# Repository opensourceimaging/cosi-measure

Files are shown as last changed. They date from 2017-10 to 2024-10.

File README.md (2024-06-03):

# COSI Measure

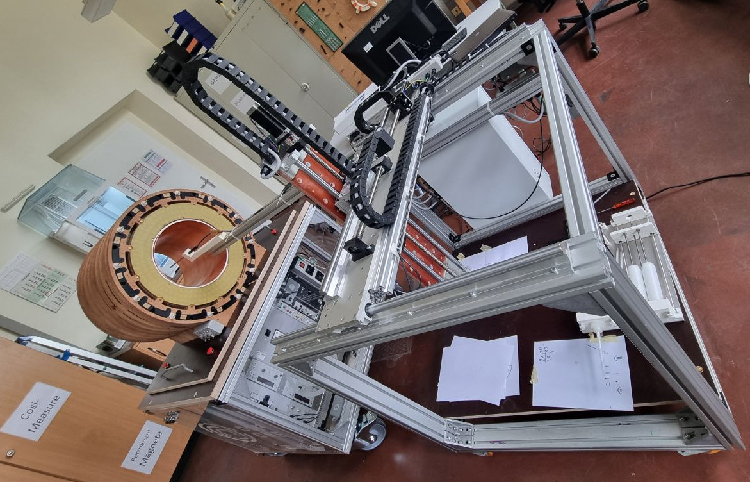
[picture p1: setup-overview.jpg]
COSI Measure


<!-- TOC -->

- [COSI Measure](#cosi-measure)
    - [Description](#description)
    - [System specifications](#system-specifications)
    - [Versions and Branches](#versions-and-branches)
    - [Contacts](#contacts)
        - [Known builds](#known-builds)
    - [Contributors alphabetical order](#contributors-alphabetical-order)
    - [Publications](#publications)
    - [Acknowledgments](#acknowledgments)
    - [License and Liability](#license-and-liability)

<!-- /TOC -->
## Description

COSI Measure is an open source multipurpose 3-axis robot operating in a large volume, that can be equipped with e.g. field mapping probes for static or dynamic field measurements (electromagnetic, temperature etc.). Submillimeter fidelity and reproducibility/backlash performance were evaluated experimentally. It can be potentially upgraded to be used as a CNC, for 3D printing or other applications, that require reproducible submillimeter movements.

## System specifications 

- Dimension: (80x90x105)cm³
- Working volume: (53x53x64)cm³
- Precision: positioning error <1mm
- Max load: ~20kg
- Applied force: 896N (91kg)
- Standalone system
- Inductive limit switches
- Emergency Stop
- Open Source Software GUI (Python)
- Estimated material costs: ~2000€

More photos and videos can be found on opensourceimaging.org: https://www.opensourceimaging.org/project/cosi-measure/ 

## Versions and Branches

You're currently viewing the `main` branch, showing ongoing development on `v2.0.*` of the COSI Measure system.\
New versions are developed in dedicated feature branches and then merged here.

The latest stable release is [v2.0](https://github.com/opensourceimaging/cosi-measure/releases/tag/v2.0).

For older, please check out the [releases overview](https://github.com/opensourceimaging/cosi-measure/releases/).

The changes between versions are summarzized in the respective release notes and documented in the [CHANGELOG](CHANGELOG.md) document.

## Contacts

General contact:
Name | Email | Institution | COSI Measure Applications
-----|-----|-----|-----|
Lukas Winter | lukas.winter@ptb.de | Physikalisch-Technische Bundesanstalt (PTB), Berlin, Germany | Magnetic field mapping of MR magnets, implant safety measurements, RF field mapping of RF coils using time-domain H- and E-field sensors, Measurements within an MR scanner, 3D printing

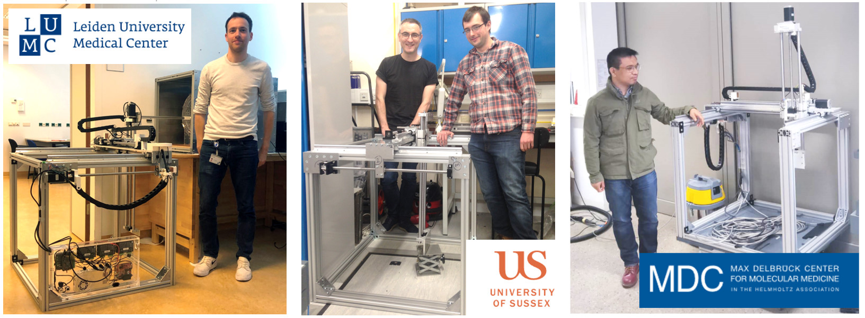
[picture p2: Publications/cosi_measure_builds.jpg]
COSI Measure Builds


### (Known) builds
Name | Email | Institution | COSI Measure Applications
-----|-----|-----|-----|
Haopeng Han | haopeng.han@mdc-berlin.de | Max-Delbrück Center for Molecular Medicine, Berlin, Germany | Temperature and RF field mapping of RF coils
Tom O'Reilly | t.o_reilly@lumc.nl | Leiden University Medical Center (LUMC), Leiden, Netherlands | Magnetic field mapping of low field MR magnets
Benjamin Menküc | benjamin.menkuec@fh-dortmund.de | University of Applied Sciences, Dortmund, Germany | Magnetic field mapping of low field MR magnets
Mark Bason | M.Bason@sussex.ac.uk | Quantum Systems and Devices, University of Sussex, Falmer, England | Magnetic field measurements
Wolfgang Kilian | Wolfgang.Kilian@ptb.de | Physikalisch-Technische Bundesanstalt (PTB), Berlin, Germany | 3D printing of phantoms

## Contributors (alphabetical order)
Nils Allek, Mark Bason, Jan Gregor Frintz, Haopeng Han, Amjad Kasabashy, Wolfgang Kilian, Ilia Kulikov, Benjamin Menküc, Tobias Mohr, Reiner Montag, Tom O'Reilly, David Shiers, Berk Silemek, Karl Stupic, Lukas Winter

## Publications
If you find this useful in your work, please cite:
[H. Han, R. Moritz, E. Oberacker, H. Waiczies, T. Niendorf and L. Winter, "Open Source 3D Multipurpose Measurement System with Submillimetre Fidelity and First Application in Magnetic Resonance", Scientific Reports, 7:13452, 2017](www.nature.com/articles/s41598-017-13824-z)

## Acknowledgments

This work is supported by the Open Source Imaging Initiative (OSI²), https://www.opensourceimaging.org/project/cosi-measure/

The project (21NRM05) has received funding from the European Partnership on Metrology, co-financed by the European Union's Horizon Europe Research and Innovation Programme and by the Participating States.

## License and Liability
The content in this repository is licensed under the CERN Open Hardware Licence Version 2 - Weakly Reciprocal, please see [LICENSE](LICENSE) for details and also check the [DISCLAIMER](DISCLAIMER.pdf)

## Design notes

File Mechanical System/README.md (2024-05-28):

# Mechanical System

Here you can find all necessary files to reproduce the COSI Measure mechanical setup.

Please read the assembly documentation first, in particular you will find some known issues or useful ideas in the comments section, which will help you reproducing the design.

## Folder: Aluplates
3D CAD models and technical drawings of the individual components.

## Folder: Complete System
3D CAD model of the complete system.

## Folder: Limit switch holder
3D CAD models of the limit switch holders

Please note that the following assembly instruction has not been updated yet to the new limit switch holders. For the new design refer to this pictures:

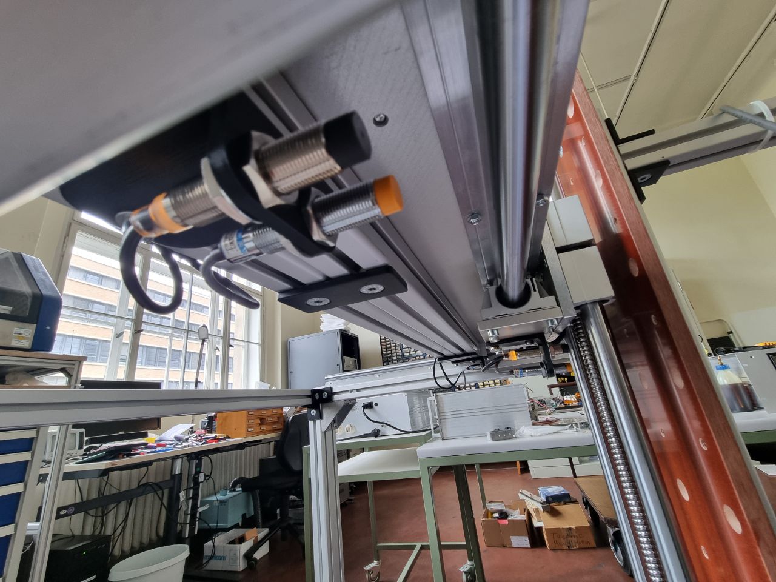
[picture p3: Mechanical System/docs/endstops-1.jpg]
Endstops 1


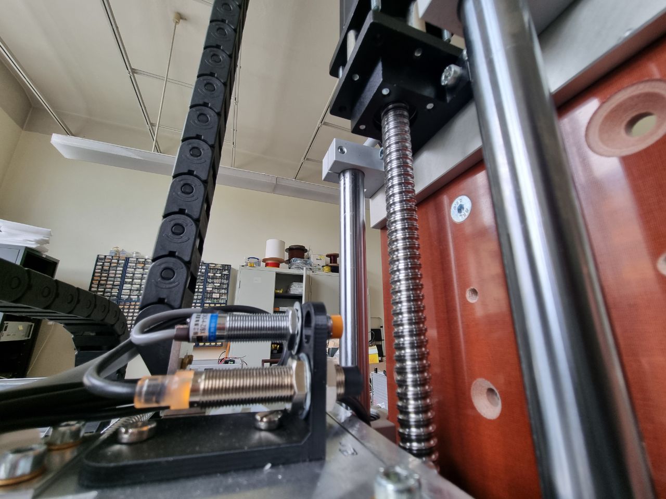
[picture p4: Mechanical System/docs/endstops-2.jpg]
Endstops 2


The outer limit switch is triggering the safe-torque-off (aka emergency stop). Thus the machine can not kill itself no matter what the software is trying to execute.

## Files: *_BoM_mechanical.ods and *_BoM_mechanical.pdf
Bill of material file for the mechanical setup. The .ods file can be opened with LibreOffice Calc (https://www.libreoffice.org/, the open source counterpart to Excel)

## Files: *_mechanical_assembly_instructions.odt and *_mechanical_assembly_instructions.pdf
Mechanical step by step assembly documentation. The .odt file can be opened with LibreOffice Writer (https://www.libreoffice.org/, the open source counterpart to Word).

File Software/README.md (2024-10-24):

# Software Getting Started

<!-- TOC -->

- [Software Getting Started](#software-getting-started)
    - [Installation](#installation)
        - [Download and Install Klipper](#download-and-install-klipper)
        - [Setting things up!](#setting-things-up)
        - [Config File](#config-file)
        - [Going into Bootloader Mode](#going-into-bootloader-mode)
        - [Flashing MCU and getting new Serial Port](#flashing-mcu-and-getting-new-serial-port)
    - [Commandline Interface](#commandline-interface)
    - [Python Software](#python-software)

<!-- /TOC -->

COSI Measure is using the open source 3D-printer firmware [klipper](https://www.klipper3d.org/). This document leads you through the installation. It´s assumed you have already installed [Raspberry-Pi-OS](https://www.raspberrypi.com/software/). We recommend the latest 64-bit Desktop version.

## Installation 

This Quick-Start-Guide is a short summary of https://www.klipper3d.org/Installation.html with some modifications for Rumba32 boards.

### 1. Download and Install Klipper

     git clone https://github.com/Klipper3d/klipper
     ./klipper/scripts/install-octopi.sh

Go to [devices/flash_mcu.sh](devices/flash_mcu.sh) and change the path in line 19 to the path of the repository above. For me line 19 is 

     19:  cd /home/cosi/klipper

### 2.1 Setting things up!

     cd klipper
     make menuconfig 

Opens a menu. Set
- Enable extra low-level configuration options
- Micro-controller Architecture (STMicroelectronics STM32)
- Processor model (STM32F446)
- Bootloader offset (32KiB bootloader)
- Clock Reference (12 MHz crystal)
- Communication interface (USB (on PA11/PA12))
- USB ids (doesnt matter. But choose something)
- no GPIO pins to set at startup ()

### 2.2 Config File

Get or write a ```printer.cfg```-file, here is mine: [devices/printer.cfg](devices/printer.cfg)

Save it as a file named "printer.cfg" in the home directory of the pi user (i.e. ```/home/cosi/printer.cfg```).

This file contains all machine configurations. Further reading: https://www.klipper3d.org/Installation.html#obtain-a-klipper-configuration-file

### 3. Going into Bootloader Mode

If not already done, install ```pigpio```for controlling the GPIO pins via the command line: 

     sudo apt-get install pigpio
     sudo systemctl enable pigpiod
     sudo systemctl start pigpiod

The shell script ```devices/flash_mcu.sh``` will set the Rumba board into bootloader mode and eventually will try to flash the MCU. Execute 

     ./backend/flash_mcu.sh

to set the board into bootloader mode. Because it doesn´t know yet the usb-id of the microcontroller it will fail to flash - ignore that for now. Search the Device ID by executing 

     lsusb

This will show up something like

     Bus 002 Device 001: ID 1d6b:0003 Linux Foundation 3.0 root hub
     Bus 001 Device 031: ID 0483:df11 STMicroelectronics STM Device in DFU Mode
     Bus 001 Device 002: ID 2109:3431 VIA Labs, Inc. Hub

So in my installatiom ```0483:df11``` is the ID of the STM-chip of Rumba32. Change line 20 in ```devices/flash_mcu.sh``` to your device ID and save the file.

### 4. Flashing MCU and getting new Serial Port

Execute ```devices/flash_mcu.sh``` again. Now it shall flash the MCU. This will eventually look something like

     Downloading to address = 0x08008000, size = 29236
     Download	[=========================] 100%        29236 bytes
     Download done.
     File downloaded successfully
     Transitioning to dfuMANIFEST state
     dfu-util: can't detach
     Resetting USB to switch back to runtime mode
     cosi@raspberrypi:~/klipper $ 

Then search for serial ports by executing 

     ls /dev/serial/by-id/*

this will return something similar to 

     /dev/serial/by-id/usb-Klipper_stm32f446xx_280058000951363131343032-if00

Copy and paste it in ```/home/cosi/printer.cfg``` to your MCU serial definition:

     [mcu]
     serial: /dev/serial/by-id/usb-Klipper_stm32f446xx_280058000951363131343032-if00

Congratulations, now you´re done. Get a coffee. Enjoy.

## Commandline Interface

Start the klipper service with executing

     sudo service klipper start

Klipper can be controlled via the following virtual serial port:

     /tmp/printer

Use 250000 Baud for communication. You can send G-code to this serial port and receive status information of the machine, refer to https://www.klipper3d.org/G-Codes.html. 

There are some custom g-code macros for disabling and enabling the drives without letting klipper loose it´s homing, for details see [printer.cfg](devices/printer.cfg) and [driver breakoutboard](../electronic-cabinet/Rumba32/Driver_BreakoutBoard/README.md). Use this commands only at standstill and never run a movement with disabled drives as this would eventually lead to false positioning.

Stop the klipper service by executing

     sudo service klipper stop

## Python Software

A python software to control CosiMeasure and a Lakeshore gaussmeter in an easy-to-use manner was developed. To get startet have a look into

     1_measurement_playground.ipynb

and 

     2_analyzing-demo.ipynb

Enjoy your day :-)

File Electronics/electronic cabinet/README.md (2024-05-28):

# COSI Measure Electronic Controls

In this folder are all the files you need to rebuild the electronic cabinet of COSI Measure. In every subfolder is a README.md as a landing page with detailed information on every subsystem.

# Building Instructions

1. Buy all needed stuff, see [bom-electronic-cabinet.csv](bom-electronic-cabinet.csv). <br>Keep in mind that there are some things missing that most of the labs have laying around e.g. screws, cables...

2. Machine all holes in the enclosure and the door, see drawings below <br>  <br> 

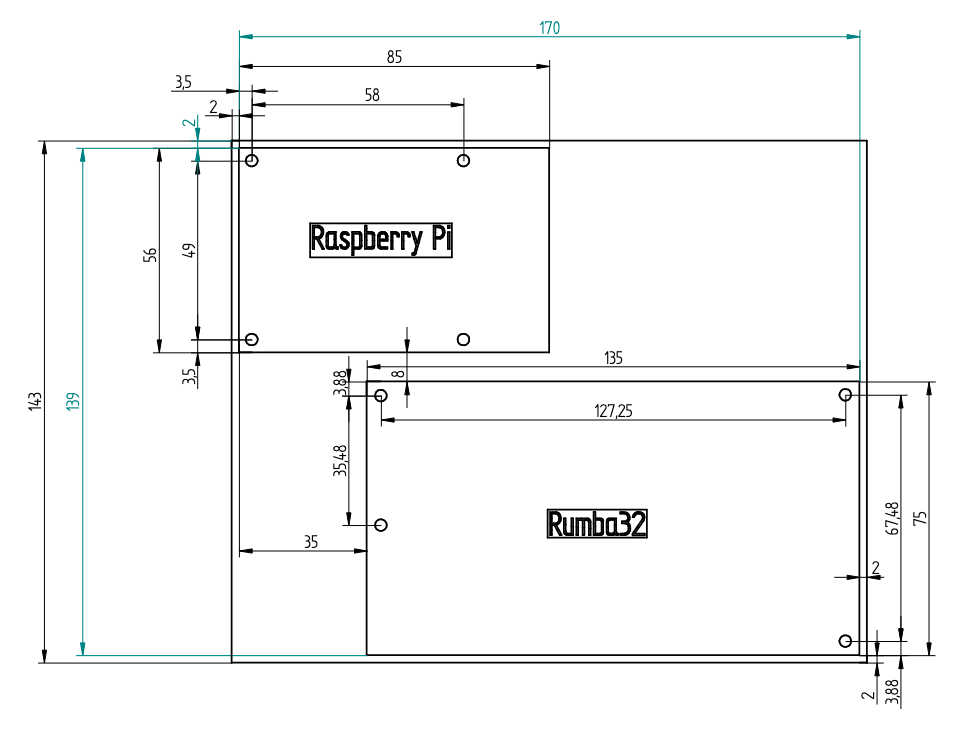
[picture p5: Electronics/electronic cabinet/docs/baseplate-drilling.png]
isolating-baseplate
3. Build and mount the baseplate for Rumba32 and RaspberryPi, see drawing below <br> 

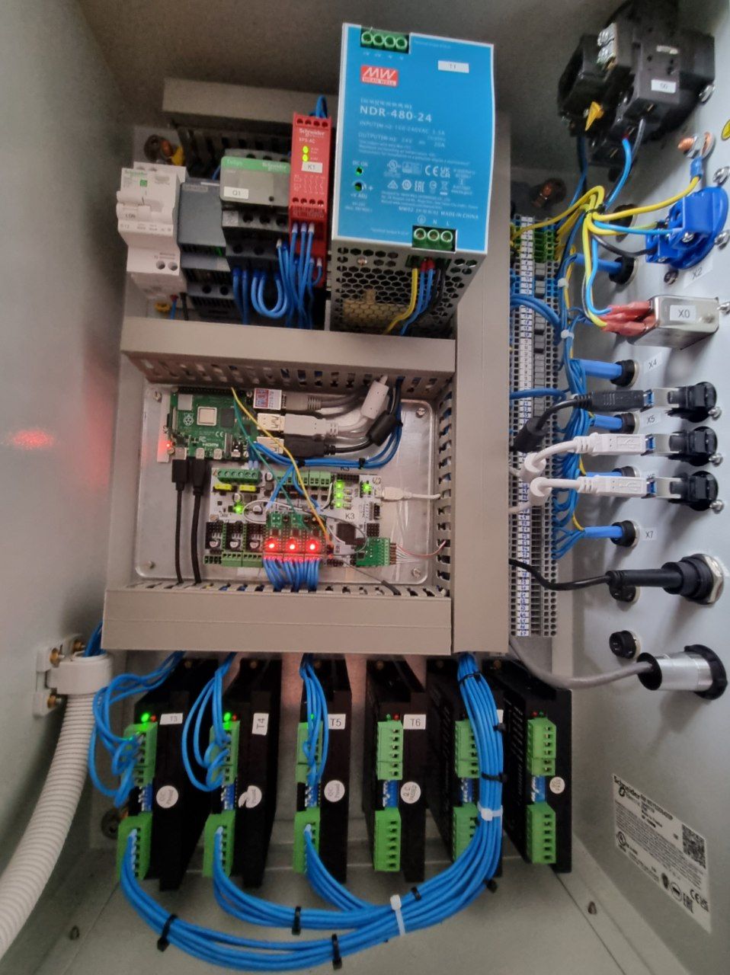
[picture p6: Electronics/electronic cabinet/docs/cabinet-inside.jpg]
4. Mount all devices to the baseplate (see picture below) and the door. <br> 

5. Build the breakoutboards, see [Levelshifter](Rumba32/Endstop_Levelshifter/README.md) and [Driver Breakoutboards](Rumba32/Driver_BreakoutBoard/README.md). Place them into the Rumba32 board.

6. mount all devices to the door and the side of the enclosure

7. Wire PE, see [schematics](schematics/README.md). Use green-yellow wire for that.

8. Wire everything else, see [schematics](schematics/README.md). Keep in mind all applicable (local) regulations. 24 V DC is wired in dark blue. 230 V AC is wired in black, the neutral wire is light blue. The 24 V power supply delivers 480 watts, so be aware to choose matching cable diameters.

9. Commissioning: 
    1. connect the machine to the enclosure. 
    2. unplug the USB power supply of the RaspberryPi!
    3. ensure/ measure that the PE is correct
    4. connect to mains
    5. ensure and test that all safety related things are working properly, e.g. that the safe-torque-off (emergency stop) is working correct
    6. Set the DIP-switches of the motor drivers:

        For T3:

        | Switch # | Comment           | Switch Position |
        |----------|-------------------|-----------------|
        | SW1      | Current Setting   | ON              |
        | SW2      | Current Setting   | ON              |
        | SW3      | Current Setting   | OFF             |
        | SW4      | Halt Current      | OFF             |
        | SW5      | Microstep Setting | ON              |
        | SW6      | Microstep Setting | OFF             |
        | SW7      | Microstep Setting | OFF             |
        | SW8      | Microstep Setting | ON              | 

        For T4:

        | Switch # | Comment           | Switch Position |
        |----------|-------------------|-----------------|
        | SW1      | Current Setting   | ON              |
        | SW2      | Current Setting   | ON              |
        | SW3      | Current Setting   | OFF             |
        | SW4      | Halt Current      | OFF             |
        | SW5      | Microstep Setting | ON              |
        | SW6      | Microstep Setting | OFF             |
        | SW7      | Microstep Setting | OFF             |
        | SW8      | Microstep Setting | ON              | 

        For T5:

        | Switch # | Comment           | Switch Position |
        |----------|-------------------|-----------------|
        | SW1      | Current Setting   | OFF             |
        | SW2      | Current Setting   | OFF             |
        | SW3      | Current Setting   | ON              |
        | SW4      | Halt Current      | OFF             |
        | SW5      | Microstep Setting | ON              |
        | SW6      | Microstep Setting | OFF             |
        | SW7      | Microstep Setting | OFF             |
        | SW8      | Microstep Setting | ON              | 
    
        You can later tune the [microstepping](https://www.analog.com/en/lp/001/optimizing-stepper-motors-microstepping.html) and the motor currents to your setup. The table above might be a good starting point. <br>Keep in mind: If you change the microstep settings on the motor drivers, you also need to change it in the [printer.cfg](../software/backend/printer.cfg)-file.<br>
        A higher microstep setting reduces the holding torque which can be compensated by more current. Having too much microsteps per full step with not enough current leads to less precise movement and increased oscillation. More info on that: https://www.monolithicpower.com/why-microstepping-isnt-as-good-as-you-think

    6. Turn off the main switch, wait until the 5V powersupply is discharged and then put back the USB power supply to RaspberryPi. Now you are ready to start with the [software](../Software/README.md).

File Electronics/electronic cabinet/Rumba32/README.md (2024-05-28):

# Rumba32

The [Rumba32](https://github.com/Aus3D/RUMBA32) is a 3D-printer mainboard with a microcontroller which is controlling the stepper motors, endstops etc. 
- It is not compatibel with industrial 12 V or 24 V limit switches so a levelshifter is needed, see [here](Endstop_Levelshifter/README.md). 
- It is not designed for external motor drivers with extended safe-torque-off (emergency stop) functionality, so breakoutboards instead of the motor drivers are needed, see [here](Driver_BreakoutBoard/README.md)
- The external motor drivers need 5 V signals, thus a little work on the Rumba32 PCB is needed, see [here](Driver_BreakoutBoard/README.md#stepper_driver_logic-jumper)
- [Klipper](https://github.com/Klipper3d/klipper) requires a temperatur signal from the nozzle and the heated bed. COSI Measure usually does not have this, so please plug two 100 k resistors to the PT100 inputs.

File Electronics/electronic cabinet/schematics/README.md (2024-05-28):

# Schematics and Terminal Plans

<!-- TOC -->

- [Schematics](#schematics)
    - [Power Distribution](#power-distribution)
    - [EmergencyStop](#emergencystop)
        - [Required Specs](#required-specs)
    - [Rumba32 and Motors](#rumba32-and-motors)
        - [NEMA color codes](#nema-color-codes)
    - [RaspberryPi](#raspberrypi)
- [Terminal Plans](#terminal-plans)
    - [X0](#x0)
    - [X1](#x1)
    - [X2](#x2)
    - [X3](#x3)
    - [X4](#x4)
    - [X5](#x5)
    - [X6](#x6)
    - [X7](#x7)
    - [X8](#x8)

<!-- /TOC -->

# Schematics

##  Power Distribution

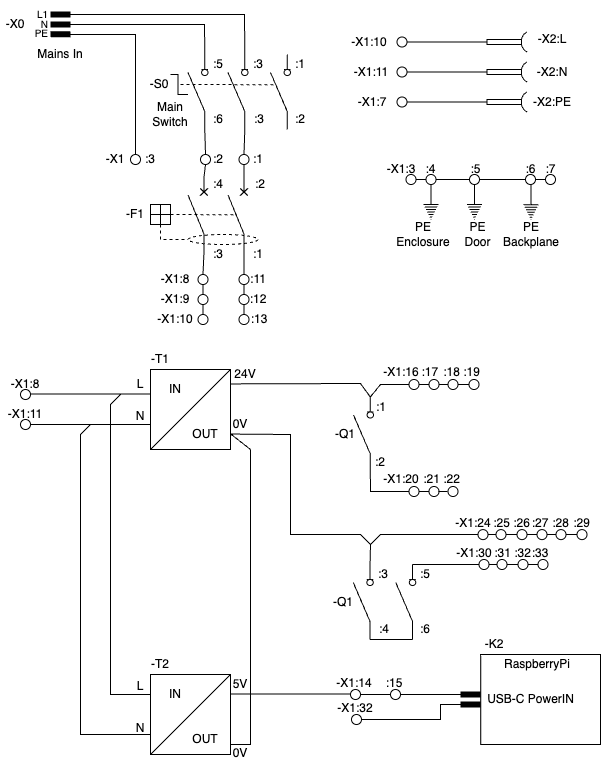
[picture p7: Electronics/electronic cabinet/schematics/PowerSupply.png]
Power Supply Schematic


The contactor $-Q1$ disconnects the motor drivers from the power supply in case of safe-torque-off (aka emergency stop). Schneider Electric has defined this way of wiring in an [application note](https://ckm-content.se.com/ckmContent/sfc/servlet.shepherd/document/download/0691H000008h5vrQAA). 

$-F1$ is an overcurrent protection with RCD. Depending to the eletcric installation of your lab and applicable regional laws it might be optional.

##  EmergencyStop

It is advisable (and most likely legal obligatory) having a safe-torque-off functionality according to EN-IS0 60204-1 so that the machine can be stopped in any cirumstance. <br>

### Required Specs
- Since the Rumba32 has no failsafe features (SIL-2 or above), the safe-torque-off must be implemented in dedicated hardware.
- to prevent unintended re-start of the drives, a dedicated safety-relais is used (-K1)
- since there are no stepper motor drivers availabe with suitable enable inputs (high-active and approved to EN-ISO 60204-1), their enable-inputs can not be used for a safe-torque-off function. So a suitable contactor (DC-3 operation for $20 \ A$ at $24 \ V_{DC}$) must be used to cut-off the power supply to the motor drivers in case of an emergency. This contactor must be selected carefully and wired according to the manufacturers guidelines to ensure safe operation.
- with some bad luck a cheap stepper motor driver can get killed by disrupting the power supply during operation due to the back-EMF of the motor. So a motor driver shall be disabled by the enable pin before interrupting the power supply connection. The used safety relais also has a NPN output which is switching faster than the mechanical relais-chain and afterwards the mechanical contactor. With this faster timing it ist possible to disable the motor driver by it´s enable input before the power gets lost. (switching off the machine by -S0 is always safe: the big $24 \ V$ power supply will slowly turn off the power and eventually take up most of the energy that might return from the drives.)
- The enable input of the motor drivers is used for disabling the drives while performing a field-measurement at an already reached location. This functionality is non safety-relevant, thus it can be implemented the easy way.

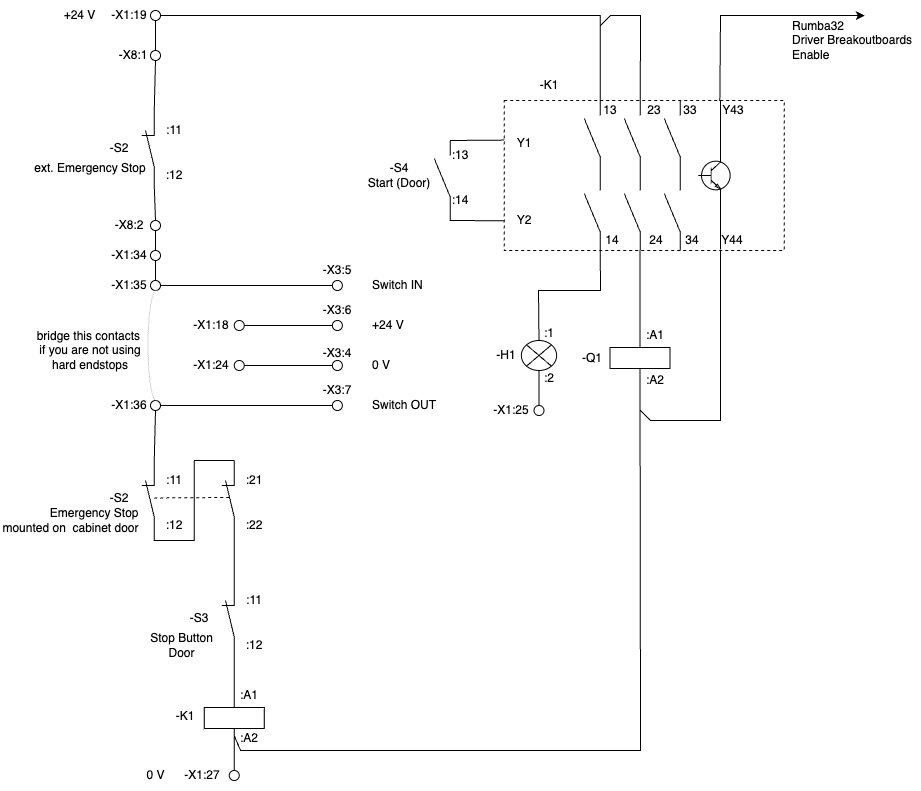
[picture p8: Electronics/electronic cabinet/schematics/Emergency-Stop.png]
Emergency Stop


Hint: The safety-relay -K1 is not in production anymore. Changes to the schematic might be neccessary for a replecement of -K1. Please update this documentation when deploying another safety relais - thanks!

## Rumba32 and Motors

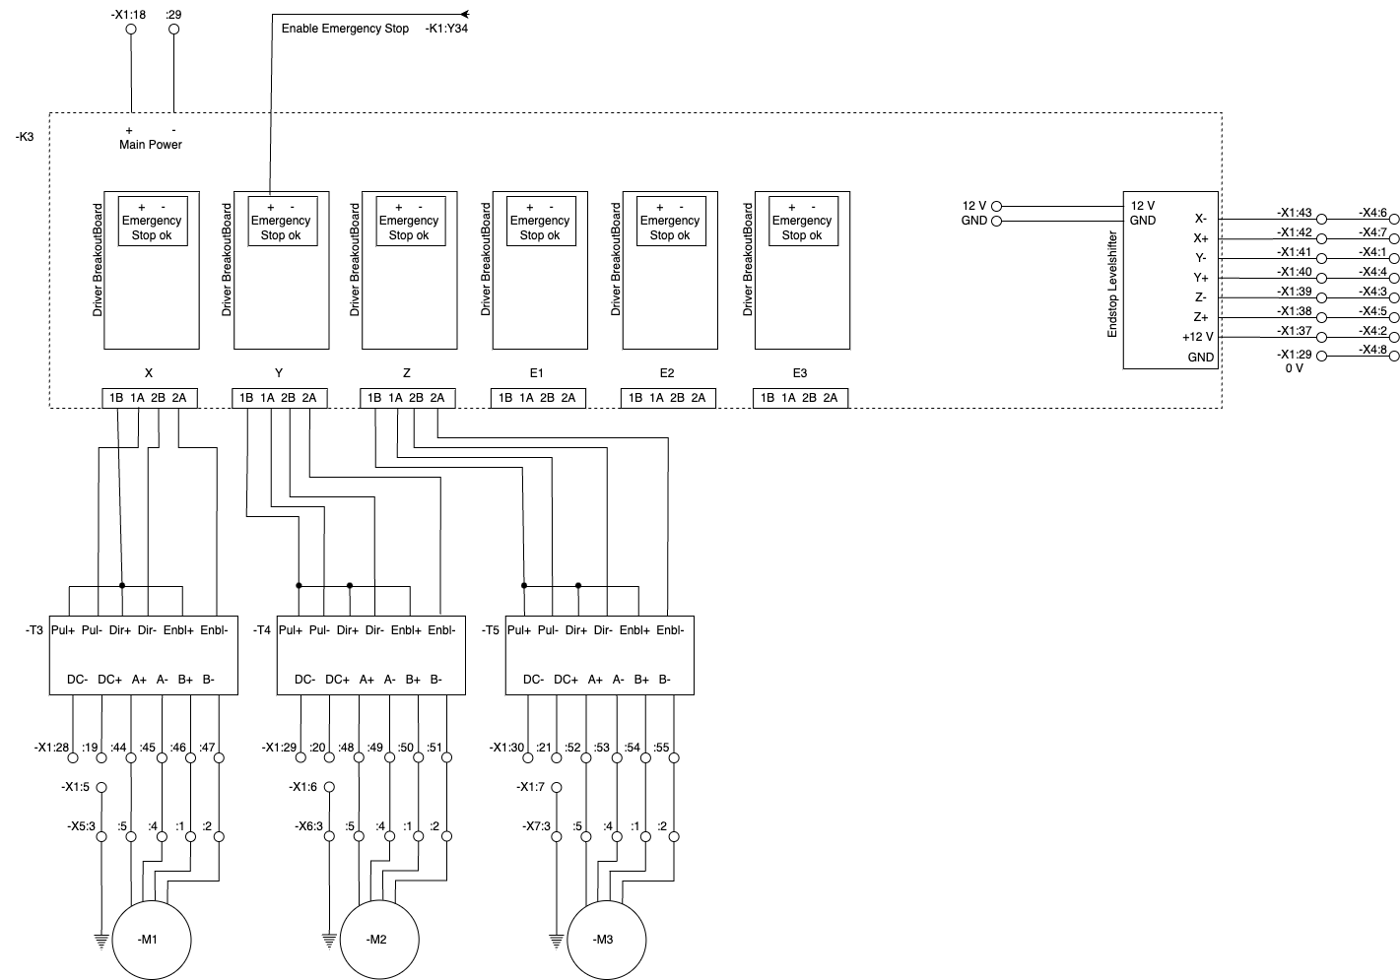
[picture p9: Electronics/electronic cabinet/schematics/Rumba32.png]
Rumba32


The [Rumba32](https://github.com/Aus3D/RUMBA32) is a 3D printer board. It is used for time-critical stuff e.g. generate the step and direction pulses for the stepper motor drivers. <br>
The Driver Breakoutboards are little custom PCBs plugged into the Rumba32, [here](../Rumba32/Driver_BreakoutBoard/README.md) is further documentation about them. 

### NEMA color codes

NEMA stepper motors usually have short color-coded wires. Unfortunately, there are multiple colorschemes used. However, some widely used color schemes are in the table below:

| Function  | scheme a  | scheme b  | cable core no | motor connector contact   |
| ----      | ----      | ----      | ----          | ---                       |
| A+        | black     |red        | 1             | :5                        |
| A-        | green     |green      | 2             | :4                        |
| B+        | red       |blue       | 3             | :1                        |
| B-        | blue      |yellow     | 4             | :2                        |
| PE/Shield | -         | -         | gn-yl         | :3                        |

Since the cores of the shielded motor cables are black, they have numbers as identifiers. The $cable \ core \ no$ in the table above is referring to the printed identifier on each core of the cable.

## RaspberryPi

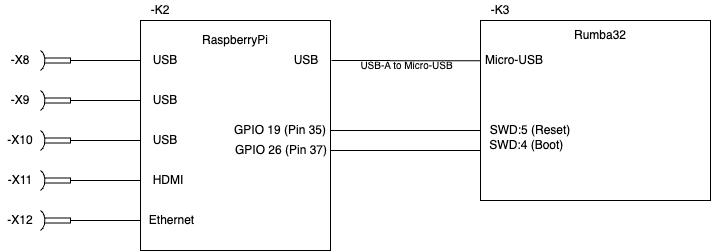
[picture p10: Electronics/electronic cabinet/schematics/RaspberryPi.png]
RaspberryPi


# Terminal Plans

## X0
Mains In Connector (IEC-60320 C13/C14)

| Contact   | connected to  |
| ----      | ----          |
| L         | -S0:3         |
| N         | -S0:5         |
| PE        | -X1:3         |

## X1

|Contact #|Comment              |Bridged to contact |Left             |Right  |
|---------|---------------------|-------------------|-----------------|-------|
|1        | L Mains             | -                 | -F1:2           | -S0:3 |
|2        | N Mains             | -                 | -F1:4           | -S0:6 |
|3        | PE                  | PE DIN-rail       | -X1:23          | -X2:PE|
|4        | PE                  | PE DIN-rail       | -T1:PE          | -X0:PE|
|5        | PE                  | PE DIN-rail       | PE Enclosure    | -X5:3 |
|6        | PE                  | PE DIN-rail       | PE Door         | -X6:3 |
|7        | PE                  | PE DIN-rail       | PE Backplane    | -X7:3 |
|8        | L, fuesd            | 9                 | -T1:L           |       |
|9        | L, fused            | 8 + 10            |                 |       |
|10       | L, fused            | 9                 |                 | -X2:L |
|11       | N, fused            | 12                | T1:N            | -X2:N |
|12       | N, fused            | 11 + 13           |                 |       |
|13       | N, fused            | 12                |                 |       |
|14       | 5V                  | 15                | -T2:V+          |       |
|15       | 5V                  | 14                | -K2:USB-V+      |       |
|16       | 24 V                | 17                | -T1: +V         |       |
|17       | 24 V                | 16 + 18           | -T1: +V         |       |
|18       | 24 V                | 17 + 19           | -K3:+           | -X3:6 |
|19       | 24 V                | 18                | -K1:13          | -X8:1 |
|20       | 24 V switched       | 21                | -T3:DC+         | -Q1:2 |
|21       | 24 V switched       | 20 + 22           |  -T4:DC+        | -Q1:2 |
|22       | 24 V switched       | 21                | -T5:DC+         |       |
|23       | 0 V / PE            | 24                | -X1:3           |       |
|24       | 0 V                 | 23 + 25           | -T1:-V          | -X3:4 |
|25       | 0 V                 | 24 + 26           | -H1:2           |       |
|26       | 0 V                 | 25 + 27           | -T2:-           |       |
|27       | 0 V                 | 26 + 28           | -K1:A2          |       |
|28       | 0 V                 | 27 + 29           | -K2:USB-GND     |       |
|29       | 0 V                 | 28                | -K3:-           | -X4:8 |
|30       | 0 V switched        | 31                | -T3: DC-        | -Q1:L3|
|31       | 0 V switched        | 30 + 32           | -T4:DC-         | -Q1:L3|
|32       | 0 V switched        | 31 + 33           | -T5:DC-         |       |
|33       | 0 V switched        | 32                | -T6:DC-         |       |
|34       | ext. Emergency-Stop | 35                |                 | -X8:2 |
|35       | -                   | 34                |                 | -X3:5 |
|36       | Hard-Endstops       |                   | -S2:11          | -X3:7 |
|37       | 12 V Endstops       |                   | -K3:12V Endstops| -X4:2 |
|38       | Endstop Z+          |                   | -K3:Z+          | -X4:5 |
|39       | Endstop Z-          |                   | -K3:Z-          | -X4:3 |
|40       | Endstop Y+          |                   | -K3:Y+          | -X4:4 |
|41       | Endstop Y-          |                   | -K3:Y-          | -X4:1 |
|42       | Endstop X+          |                   | -K3:+           | -X4:7 |
|43       | Endstop X-          |                   | -K3:-           | -X4:6 |
|44       | -M1:A+              |                   | -T3:A+          | -X5:5 |
|45       | -M1:A-              |                   | -T3:A-          | -X5:4 |
|46       | -M1:B+              |                   | -T3:B+          | -X5:1 |
|47       | -M1:B-              |                   | -T3:B-          | X5:2  |
|48       | -M2:A+              |                   | -T4:A+          | -X6:5 |
|49       | -M2:A-              |                   | -T4:A-          | -X6:4 |
|50       | -M2:B+              |                   | -T4:B+          | -X6:1 |
|51       | -M2:B-              |                   | -T4:B-          | X6:2  |
|52       | -M3:A+              |                   | -T5:A+          | -X7:5 |
|53       | -M3:A-              |                   | -T5:A-          | -X7:4 |
|54       | -M3:B+              |                   | -T5:B+          | -X7:1 |
|55       | -M3:B-              |                   | -T5:B-          | -X7:2 |
|56       |                     |                   |                 |       |
|57       |                     |                   |                 |       |
|58       |                     |                   |                 |       |
|59       |                     |                   |                 |       |
|60       |                     |                   |                 |       |
|61       |                     |                   |                 |       |
|62       |                     |                   |                 |       |
|63       |                     |                   |                 |       |

The contacts 56 to 63 are reserved for future upgrades, e.g. additional axis.

## X2

External Power Socket

| Contact   | connected to  |
| ----      | ----          |
| L         | -X1:10        |
| N         | -X1:11        |
| PE        | -X1:7         |

## X3
Hard-Endstops Connector

| Contact | Comment    | Connected To |
|---------|------------|--------------|
| 1       | -          | -            |
| 2       | -          | -            |
| 3       | -          | -            |
| 4       | 0 V        | -X1:24       |
| 5       | Switch IN  | -X1:35       |
| 6       | 24 V       | -X1:18       |
| 7       | Switch OUT | -X1:36       |
| 8       | -          | -            |

## X4
Endstops Connector

| Contact | Comment | Connected To |
|---------|---------|--------------|
| 1       | Y-      | -X1:41       |
| 2       | +12 V   | -X1:37       |
| 3       | Z-      | -X1:39       |
| 4       | Y+      | -X1:40       |
| 5       | Z+      | -X1:38       |
| 6       | X-      | -X1:43       |
| 7       | X+      | -X1:42       |
| 8       | 0 V     | -X1:29       |

## X5
Motor X-Axis Connector

| Contact | Comment     | Connected To |
|---------|-------------|--------------|
| 1       | B+          | -X1:46       |
| 2       | B-          | -X1:47       |
| 3       | PE & Shield | -X1:5        |
| 4       | A-          | -X1:45       |
| 5       | A+          | -X1:44       |
| 6       | -           | -            |

## X6
Motor Y-Axis Connector

| Contact | Comment     | Connected To |
|---------|-------------|--------------|
| 1       | B+          | -X1:50       |
| 2       | B-          | -X1:51       |
| 3       | PE & Shield | -X1:6        |
| 4       | A-          | -X1:49       |
| 5       | A+          | -X1:48       |
| 6       | -           | -            |

## X7
Motor Z-Axis Connector

| Contact | Comment     | Connected To |
|---------|-------------|--------------|
| 1       | B+          | -X1:54       |
| 2       | B-          | -X1:55       |
| 3       | PE & Shield | -X1:7        |
| 4       | A-          | -X1:53       |
| 5       | A+          | -X1:52       |
| 6       | -           | -            |

## X8
External Emergency Stop Connector

| Contact | Comment     | Connected To |
|---------|-------------|--------------|
| 1       | +24 V   	| -X1:19       |
| 2       | Switch Out  | -X1:34       |
| 3       | - 			| -            |

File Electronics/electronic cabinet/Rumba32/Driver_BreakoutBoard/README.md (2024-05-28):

# Driver Breakout Board

<!-- TOC -->

- [Driver Breakout Board](#driver-breakout-board)
    - [Enable Logic](#enable-logic)
    - [Schematic](#schematic)
    - [BOM](#bom)
    - [Setting jumpers on Rumba32](#setting-jumpers-on-rumba32)
        - [STEPPER_DRIVER_LOGIC JUMPER](#stepper_driver_logic-jumper)
        - [Additional Software Enable Jumpers](#additional-software-enable-jumpers)

<!-- /TOC -->

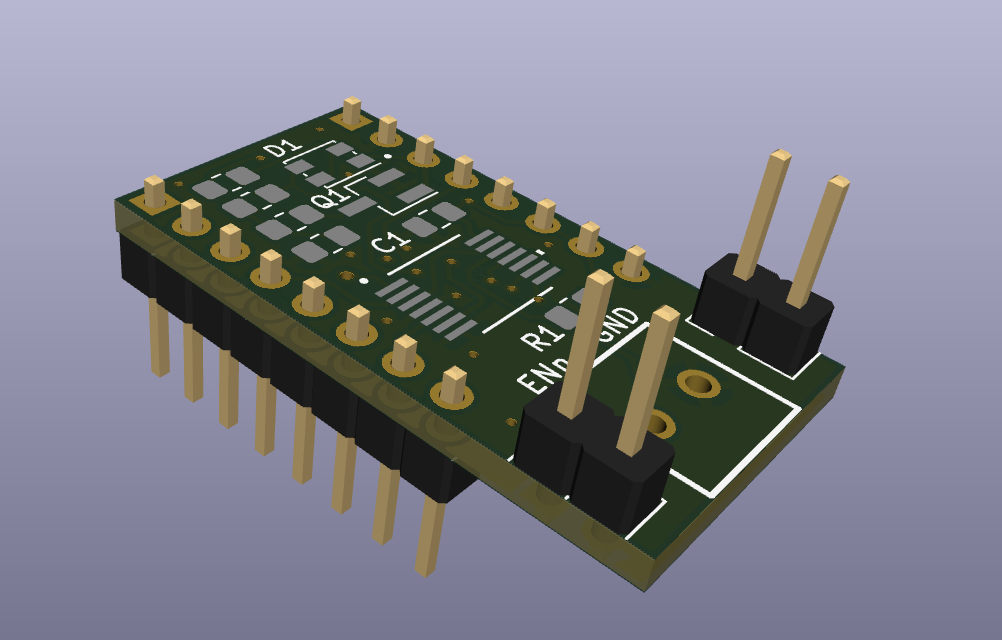
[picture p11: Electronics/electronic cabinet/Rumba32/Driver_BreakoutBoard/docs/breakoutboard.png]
Breakout Board


This breakoutboard can be placed to the motor driver slots into the Rumba32 board. 
It is useful for wiring the step, direction and enable pins via the motor connector to external motor drivers. In addition it supports an easy way of integrating a drive-enable functionality.

## Enable Logic

There can be current on the drives, if 
- The Firmware enables the drives and
- some control pins are low (furhter explanation below) and
- Emergency Stop Relais provides it's NPN-ok signal ($0 \ V$).
- Contactor -Q1 is closed (no safe-torque-off)

Many 3D-printing firmwares are not designed for switching off the drives completly while executing a G-code file. But COSI-Measure is meant to perform magnetic measurements, so it must not disturb the measurements with noisy motor currents while performing a measurement.

A convenient workaround for Klipper is to switch on and off some extra GPIO Pins, that are wired to the hardware-enable-logic. In case you are doing something different and you do not need this feature, feel free to ignore it. Default of these Pins is low, which is also the enabled state. For details about it see the [printer.cfg](../../../software/backend/printer.cfg) file line 275-317. The drives can be enabled and disabled with g-code macros while keeping the homing active.

The NPN-ok-signal from the emergency stop relais can be daisy-chained with standard 2.54 mm jumpers to the next breakout board.

The enable input of the motordriver is not meant for a safe-torque-off function (emergency stop). Safe-torque-off is implemented in hardware (mechanical relais, contactors etc.), see [schematics](../../schematics/README.md#emergencystop). 
Anyway, to prevent driver malfunction the driver will be disabled with semiconductor only circuits before the power supply of the driver will be disconnected. The delay is coming from the slower reaction of mechanical contactors and relais, so no dedicated timing module is needed.

## Schematic

Schematic

## BOM

This Bill-of-Materials is for 1 breakout board only. You need one breakout board for each motor with external motor drivers, usually 3 in total (depending to your setup).

| #  | Designator | Quantity | Comment              | Man. Part-No       | Link                                                                                            |
|----|------------|----------|----------------------|--------------------|-------------------------------------------------------------------------------------------------|
| 1  | C1         | 1        | 10 nF, 0805          | C0805C103K2RECAUTO | <https://www.digikey.de/de/products/detail/kemet/C0805C103K2RECAUTO/8646745>                    |
| 2  | D1         | 1        | Dual LED red/green   | AAA3528ESGCT       | <https://www.digikey.de/de/products/detail/kingbright/AAA3528ESGCT/7318936>                     |
| 3  | IC1        | 1        | OR-Gate              | SN74ACT32PWR       | <https://www.digikey.de/en/products/detail/texas-instruments/SN74ACT32PWR/376063>               |
| 4  | J1, J2     | 2        | 8 pin header 2.54    | 61300811121        | <https://www.digikey.de/de/products/detail/w%C3%BCrth-elektronik/61300811121/4846839>           |
| 5  | J3, J5     | 2        | 2 pin header 2.54    | 61300211121        | <https://www.digikey.de/de/products/detail/w%C3%BCrth-elektronik/61300211121/4846823>           |
| 6  | J4         | 1        | 2 pos screw terminal | 0393570002         | <https://www.digikey.de/de/products/detail/molex/0393570002/946543>                             |
| 7  | Q1         | 1        | NPN Transistor       | MMBT3904           | <https://www.digikey.de/de/products/detail/micro-commercial-co/MMBT3904-TP/717280>              |
| 8  | R1         | 1        | 47 kOhm, 0805        | WR08X473 JTL       | <https://www.digikey.de/de/products/detail/walsin-technology-corporation/WR08X473-JTL/13240617> |
| 9  | R2         | 1        | 270 Ohm, 0805        | RMCF0805JT270R     | <https://www.digikey.de/de/products/detail/stackpole-electronics-inc/RMCF0805JT270R/1757887>    |
| 10  | R3, R5    | 2        | 200 Ohm, 0805        | RMCF0805FT200R     | <https://www.digikey.de/de/products/detail/stackpole-electronics-inc/RMCF0805FT200R/1760343>    |
| 11 | R4         | 1        | 1.2 kOhm, 0805       | RMCF0805JT1K20     | <https://www.digikey.de/de/products/detail/stackpole-electronics-inc/RMCF0805JT1K20/1757811>    |
| 12 | -          | 3        | 2.54 mm jumper       | QPC02SXGN-RC       | <https://www.digikey.de/en/products/detail/sullins-connector-solutions/QPC02SXGN-RC/2618262>    |

## Setting jumpers on Rumba32

### STEPPER_DRIVER_LOGIC JUMPER 

The STEPPER_DRIVER_LOGIC jumper (see picture below) selects the logic voltage supplied to all stepper driver
sockets. By default, it is configured so that 3.3V is supplied to the stepper drivers. However, since the external motor drivers need 5 V, the track between the centre and 3V pad should be cut, and a solder joint placed over the 5V and centre pad. <br>
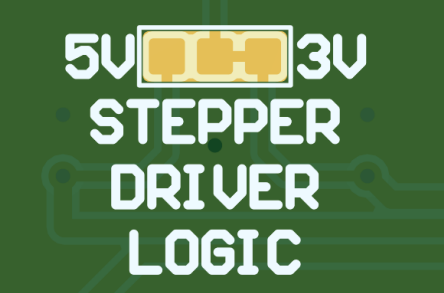
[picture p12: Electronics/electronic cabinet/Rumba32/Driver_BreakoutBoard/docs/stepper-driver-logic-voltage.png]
voltage selection
 <br>
(picture and parts of the text above borrowed from https://github.com/Aus3D/RUMBA32/blob/master/Resources/Manual/RUMBA32%20V1.1%20User%20Manual%20-%20REV%20A.pdf, License: GPLv2)

### Additional Software Enable Jumpers
Set the jumpers beneath the breakoutboards as seen in the picture below (blue):

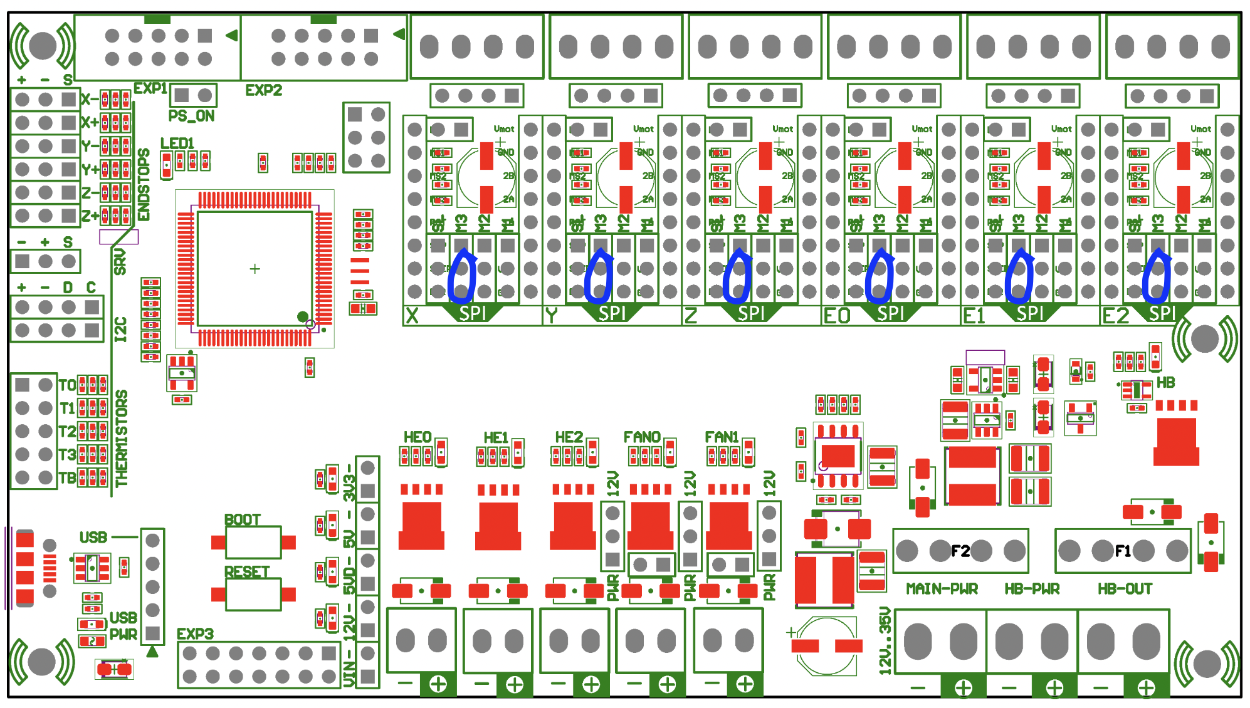
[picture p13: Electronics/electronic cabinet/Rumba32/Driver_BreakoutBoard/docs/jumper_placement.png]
jumper placement
 <br>
(Picture borrowed and modified from https://github.com/Aus3D/RUMBA32?tab=readme-ov-file, License: GPLv2)

These jumpers are connecting some GPIO-Pins to the enable logic of this breakout board.

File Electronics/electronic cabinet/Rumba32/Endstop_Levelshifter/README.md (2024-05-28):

# Endstop BreakoutBoard

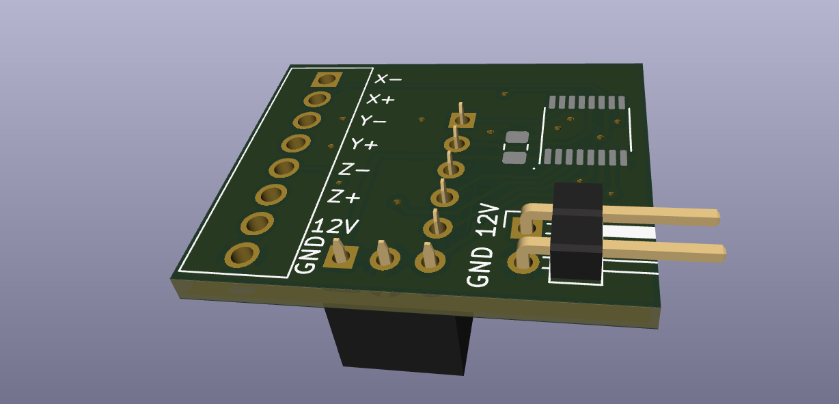
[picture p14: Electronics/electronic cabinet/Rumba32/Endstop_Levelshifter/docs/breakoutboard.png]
Breakout Board


This breakoutboard needs to be placed into Rumba32 Endstop connector. It is a levelshifter for the 12 V Endstops. 

12V is supplied by Rumba32, you need to connect the 12V Pins of Rumba32 to J4 of this breakout board.

## Schematic

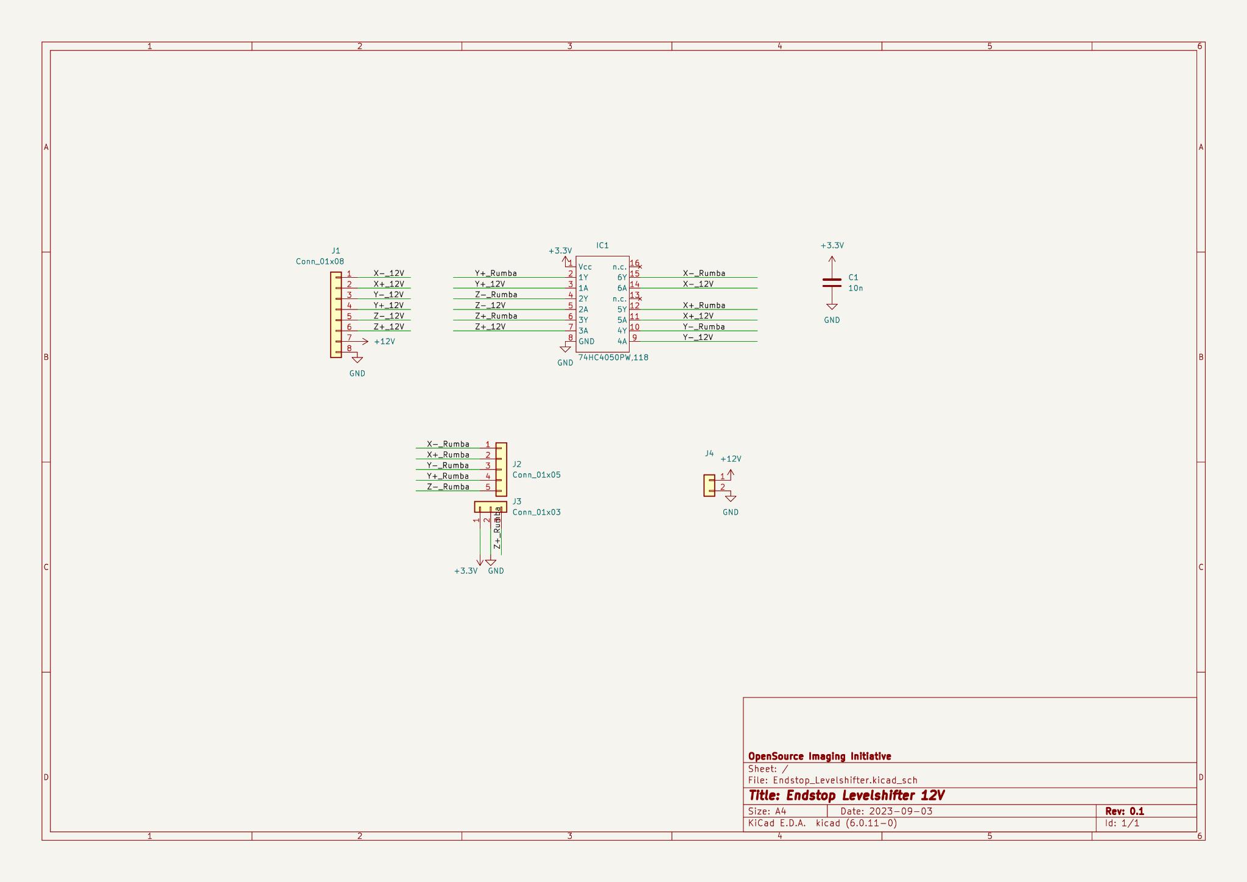
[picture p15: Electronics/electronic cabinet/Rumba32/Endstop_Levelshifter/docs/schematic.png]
Schematic


## BOM

| ld 	| Designator 	| Quantity 	| Comment           	| Manufacturer Part No 	| Link Digikey                                                                          	|
|----	|------------	|----------	|-------------------	|----------------------	|---------------------------------------------------------------------------------------	|
| 1  	| J1         	| 1        	| Screw Terminal    	| 691210910008         	| https://www.digikey.de/de/products/detail/w%C3%BCrth-elektronik/691210910008/11478428 	|
| 2  	| C1         	| 1        	| 10n               	| C0805C103K2RECAUTO   	| https://www.digikey.de/de/products/detail/kemet/C0805C103K2RECAUTO/8646745            	|
| 3  	| J4         	| 1        	| 2 Pin Header 2.54 	| 0022289020           	| https://www.digikey.de/de/products/detail/molex/0022289020/3158803                    	|
| 4  	| J3         	| 1        	| 3 Pin Header 2.54 	| 801-87-003-10-001101	| https://www.digikey.de/de/products/detail/preci-dip/801-87-003-10-001101/3757430      	|
| 5  	| J2         	| 1        	| 5 Pin Header 2.54 	| 801-87-005-10-001101 	| https://www.digikey.de/de/products/detail/preci-dip/801-87-005-10-001101/3757433      	|
| 6  	| IC1        	| 1        	| Buffer            	| 74HC4050PW,118       	| https://www.digikey.de/de/products/detail/nexperia-usa-inc/74HC4050PW-118/1230398     	|

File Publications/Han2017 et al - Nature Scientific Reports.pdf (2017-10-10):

Open Access This article is licensed under a Creative Commons Attribution 4.0 International License, which permits use, sharing, adaptation, distribution and reproduction in any medium or format, as long as you give appropriate credit to the original author(s) and the source, provide a link to the Creative Commons license, and indicate if changes were made. The images or other third party material in this article are included in the article’s Creative Commons license, unless indicated otherwise in a credit line to the material. If material is not included in the article’s Creative Commons license and your intended use is not permitted by statutory regulation or exceeds the permitted use, you will need to obtain permission directly from the copyright holder. To view a copy of this license, visit http://creativecommons.org/licenses/by/4.0/.

Haopeng | Han,
Raphael | Moritz,
Eva | Oberacker,
Helmar | Waiczies,
Thoralf | Niendorf,
Lukas | Winter,
Email Lukas.Winter@mdc-berlin.de

Berlin Ultrahigh Field Facility (B.U.F.F.), Max-Delbrück Center for Molecular Medicine in the Helmholtz Association, Berlin, Germany

Experimental and Clinical Research Center (ECRC), a joint cooperation between the Charité and the Max Delbrück Center for Molecular Medicine, Berlin, Germany

MRI.TOOLS GmbH, Berlin, Germany

Received: 23 May 2017 / Accepted: 29 September 2017

1

1

1

3

1,2,3

1✉

1

2

3

e.Proofing | http://eproofing.springer.com/journals_v2/printpage.php?token=UyQ...
1 of 29 | 06.10.2017 14:15

Magnetic resonance imaging (MRI) is the mainstay of diagnostic imaging, a versatile instrument for clinical science and the subject of intense research interest. Advancing clinical science, research and technology of MRI requires high fidelity measurements in quantity, location and time of the given physical property. To meet this goal a broad spectrum of commercial measurement systems has been made available. These instruments frequently share in common that they are costly and typically employ closed proprietary hardware and software. This shortcoming makes any adjustment for a specified application difficult if not prohibitive. Recognizing this limitation this work presents COSI Measure, an automated open source measurement system that provides submillimetre resolution, robust configuration and a large working volume to support a versatile
range | of | applications. | The | submillimetre | fidelity | and
reproducibility/backlash performance were evaluated experimentally. Magnetic field mapping of a single ring Halbach magnet, a 3.0 T and a 7.0 T MR scanner as well as temperature mapping of a radio frequency coil were successfully conducted. Due to its open source nature and versatile construction, the system can be easily modified for other applications. In a resource limited research setting, COSI Measure makes efficient use of laboratory space, financial resources and collaborative efforts.

Magnetic resonance imaging (MRI) is a vital clinical tool for diagnosis and for guiding therapy, which has been described as the single most important medical innovation[1, 2]. MRI is a versatile instrument for clinical science and the subject of intense research interest. Research directions focus on conventional and emerging applications[3, 4, 5, 6, 7, 8, 9, 10, 11, 12, 13, 14, 15, 16, 17] facilitated by enabling technology including new magnet design[18, 19, 20], gradient coil developments[21, 22], novel radio frequency technology[23, 24, 25, 26, 27, 28, 29], techniques for probing and shimming magnetic fields[30, 31], transmission field mapping and shaping[32, 33], electric property tomography[34], thermal interventions and RF heating[35, 36, 37], magnetic resonance safety and MR compatibility[38, 39, 40, 41, 42]. Advancing this research requires high fidelity measurements in quantity and location of the given physical property, including E-fields, H-fields and

temperature.

To meet this need a portfolio of instruments supporting temperature, E-field or H-field probes are commercially available. The ubiquity of and enthusiasm for these instruments is strongly hampered because they are costly and commonly customized if not limited to a specified application. Mapping a tiny volume might be sufficient for E- or H-field measurements of small and mid-size RF antennae[43]. Yet, examining the characteristics of large volume or whole body RF antennae requires enhanced coverage including the whole magnet bore. The spatial resolution requirements for E- or H-field measurements in test objects might be sufficient within a centimetre resolution. MR safety applications like RF induced E-field or temperature measurements of subtle passive conductive medical implants might require sub-millimetre resolution though[39, 44]. The performance of RF coils or gradient coil inserts can be evaluated outside of the MR magnet. Yet, main magnetic field characterization or measurements during MRI scans might require sensors being positioned and moved inside the MR magnet. Supporting a broad range of applications requires the capability to position the measurement device horizontally and vertically.

Developing a measurement system that meets the requirements of spatial fidelity without the use of any magnetic components constitutes a challenge, is costly and might come with the caveat of offsetting if not losing its versatility and capability to support a broad range of applications. Common 3D printers or XYZ tables can be potentially used in conjunction with E-field and H-field probes to map the field of RF coils, however they are not strong enough to facilitate long probes that reach into the MR scanner bore, are limited by the mapping volume or lack an open source nature in order to adjust the system for the intended application[41, 43, 45].

Recognizing these limitations this work presents an automated open source measurement system that provides submillimetre resolution for a material cost of ~2000€. The development of this measurement system is part of the cost effective open source imaging (COSI) initiative aiming to build an affordable open source MR system and dedicated research hardware[46, 47, 48]. COSI Measure can be used together with various probes including electromagnetic, temperature and ultrasound sensors in magnetic resonance research and in related fields. Due to its open source nature and versatile construction, the system can be easily modified for other applications such as computer numeric control machinery, 3D printing, surface-mount device soldering etc.

The open source nature of COSI Measure (updates will be posted on www.opensourceimaging.org) allows the research community to share and enjoy improvements, upgrades and modifications of the system, which simplifies and accelerates the reproducibility of research results. In a resource limited research setting, COSI Measure makes efficient use of laboratory space, financial resources and collaborative efforts.

The mechanical subsystem has been designed in a 3D CAD (computer-aided design) model using SketchUp Make (version 15.3.331, Trimble Navigation Limited, Sunnyvale, CA, USA). It is designed as a three axis linear stage[49, 50, 51], with a robust aluminium based frame[52]. A strong and robust setup was intended to accommodate a broad spectrum of measurement, construction or scientific tools such as electromagnetic field probes, temperature sensors, drills, plotters, saws, pipettors etc. The base frame is made of 11 aluminium profiles and has the dimensions of (880 × 960 × 840) mm³, so that it is able to pass through a door (standard width = 940 mm). Three ball screws (one for each axis) which consist of 5 mm threaded shafts and ball bearings have been used to translate rotational motion to linear motion. A second ball screw can be mounted along the x-axis for applications that need higher forces (e.g. CNC applications). The advantages of using ball screws are high precision and good reproducibility, which are key features for measuring physical parameters. We use linear bearings and supported rails to support the mechanical movement for the x- and y-axis while precision shafts and linear bearings are used to guide the movement along the z-axis. Ball screws and floated bearings are mounted on customized aluminium (10 mm thickness) plates. Limit-switch- and cable-chain-holders were designed in 3D CAD and 3D printed with ABS (acrylonitrile butadiene styrene) material. A movable lift table allows mobility of the system and provides the possibility of adjusting the height of the machine.

Assembly instructions, 3D CAD models of the complete system, the aluminium plates and limit switch holders, as well as the numbered part list with cost, quantity and vendor are available in the files provided, with an overview given in Table 1.

Table 1
Design files for the mechanical subsystem.
assembly_instructions.docx | This file describes the assembly process of the
| machine step by step.
Aluplates | This folder contains all the SketchUp design files for the aluminum plates. Files in this folder are named in the format of Pn_XxYxZ, with Pn being the name of the plate, X, Y and Z being the dimensions of the plate.
Limit Switch holder | This folder contains all the design files for the limit switch and cable chain holders.
complete_system.skp | This file is the SketchUp design for the whole system.
partlist.xlsx | This file contains information of all the components used in the mechanical subsystem.

The electronic subsystem consists of a community-supported open source embedded computer Beagle Bone Black (BBB)[53], a cape board BeBoPr++ (http://elinux.org/BeBoPr%2B%2B), a power management board, a power supply unit (PSU), NEMA23 stepper motors, DM542A motor drivers and LJ12A3-4-Z/BX inductive proximity sensors. The schematic of the functionality is displayed in Fig. 1. The Beagle Bone Black is the heart of the electronic subsystem. It is equipped with an AM3358 (Texas Instruments, Dallas, TX, USA) which is a 1 GHz ARM Cortex-A8 System-on-Chip processor, 512MB DDR3 SDRAM (double data rate type three synchronous dynamic random-access memory) and versatile input/output options. The AM3358 is particularly suitable for real-time tasks like controlling motors since it contains two 32-bit microcontrollers which form the programmable real-time unit subsystem and industrial communication subsystem (PRU-ICSS). The BBB has 65 GPIO (general-purpose input/output) pins allowing for flexible application. The cape board BeBoPr ++ is designed to work with the BBB, which can be mounted on top. It is equipped with interfaces to connect up to 5 motor drivers, 6 limit switches, thermos sensors and PWM (pulse-width modulation) outputs for a possible CNC/3D-printing application. The BeBoPr++ also provides power (5 V direct current (DC)) for the BBB. All the signals interfacing BBB are protected on the BeBoPr++ so that the BBB would not be damaged. An emergency stop button was included for hardware protection and safety reasons. A power management board (Fig. 2 shows its block diagram) was designed with the open source EDA (electronic design automation) tool KiCad (version 4.0.2, kicad-pcb.org) to distribute the power in COSI Measure and to provide logic level conversion for the inductive proximity sensors. AC (alternating current) power is distributed to the PSU for the motors through a relay on this board. There is an AC/DC module on the board to generate 12 V DC power supply for the BeBoPr++. Two push buttons connected to a complex programmable logic device (CPLD: XC2C64A, Xilinx, San Jose, CA, USA) are used to control the AC and DC power on and off independently allowing turning the BBB on and leaving the motors off in order to save energy. Delay circuits are implemented in the CPLD so that a short press on the buttons turns the power on while a long press turns the power off. Six inductive proximity sensors with a detection distance of 4 mm were used as limit switches to detect the working range of COSI Measure. These sensors require a minimum working voltage of 6 V DC which is higher than the interface logic (5 V transistor–transistor logic (TTL)) on the BeBoPr++. Hence six logic shifters were implemented on the power management board. We used three NEMA23 stepper motors (3 A@36 V, 3NM holding torque, 1.8° step angle) together with three DM542A motor drivers, which allow 2-128x micro-stepping leading to a theoretical precision limit of ~200 nm and a half holding current operation for power saving. We chose to use stepper motors mainly for three reasons: 1) Stepper motors provide a submillimetre resolution. 2) They are easy to operate and to deploy. Stepper motors have positional control via its nature of rotation by fractional increments, so that no feedback (closed-loop) is needed for accurate positioning. 3) Stepper motors are less expensive than alternatives such as servo motors or piezoelectric/ultrasound motors. The motors and drivers are supplied by an AC/DC power supply unit (36 V, 9.7 A). The electronic components have been integrated into a PC (personal computer) chassis for easy transportation. An HDMI (high-definition multimedia interface) monitor, a keyboard, a mouse as well as an RJ45 Ethernet cable were connected to the BBB via the chassis, so they form a complete standalone computing system. Cables from the stepper motors and limit switches were inserted into cable chains and soldered to miniature circular connectors. This allows flexibility in removing the standalone COSI Measure PC to be unplugged and used for other applications.

Figure 1
Schematic of the electronic subsystem. 3 stepper motors are controlled by

Beagle Bone Black (BBB) through the BeBoPr++ base board and the motor drivers. 6 limit switches are connected to the BBB through level shifters on the power management board. An emergency switch is connected for safety reasons. The power supply unit and the power management board are in charge of generating, distributing and managing the power for the system. Peripherals such as monitor, keyboard and mouse are also connected.

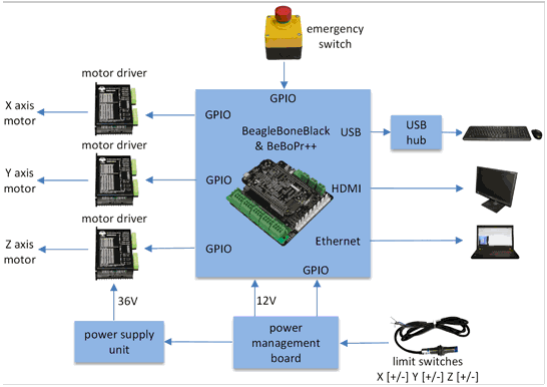
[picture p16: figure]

Figure 2
Block diagram of the power management board. The AC/DC module is used to generate the 12 V DC power for BeBoPr++/ BBB, level shifters and limit switches. The DC/DC circuit converts 12 V input to 5 V for level shifters and the CPLD. Two push buttons connected to the CPLD are used for controlling the power supply for motors and BeBoPr++/BBB separately by manipulating the relays.

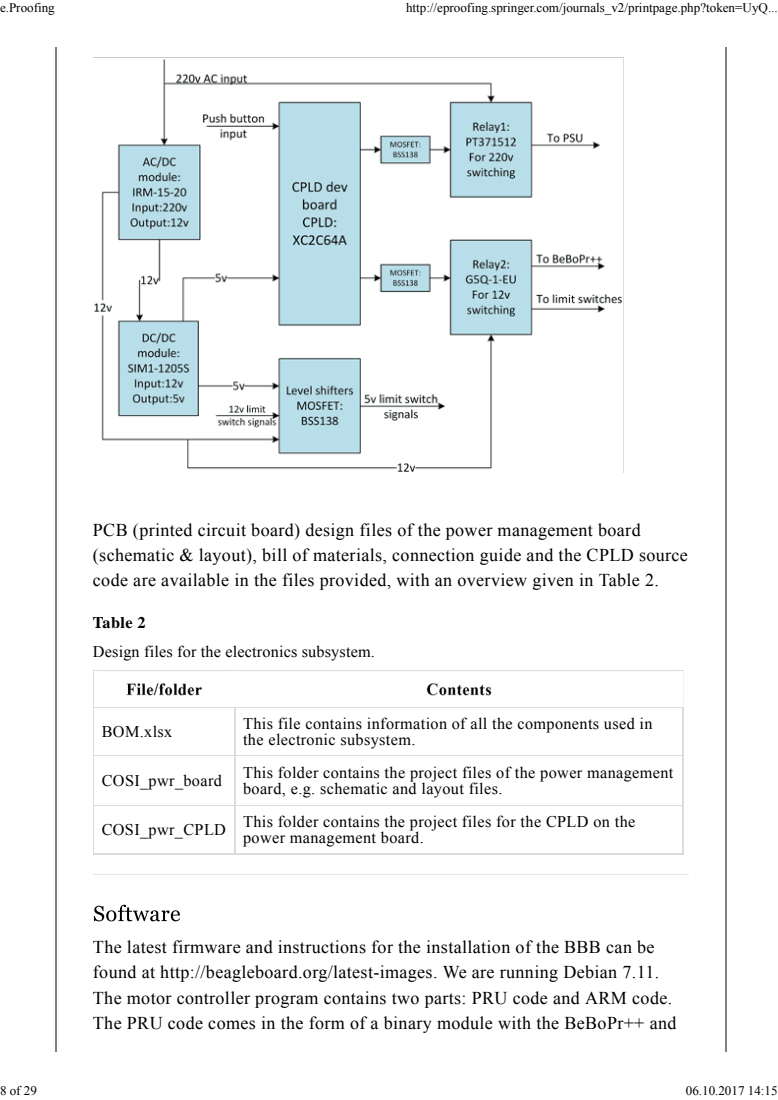
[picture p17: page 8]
BOM.xlsx; This file contains information of all the components used in

PCB (printed circuit board) design files of the power management board
(schematic & layout), bill of materials, connection guide and the CPLD source
code are available in the files provided, with an overview given in Table 2.

Table 2
Design files for the electronics subsystem.

the electronic subsystem.

COSI_pwr_board | This folder contains the project files of the power management board, e.g. schematic and layout files.

COSI_pwr_CPLD | This folder contains the project files for the CPLD on the power management board.

The latest firmware and instructions for the installation of the BBB can be
found at http://beagleboard.org/latest-images. We are running Debian 7.11.
The motor controller program contains two parts: PRU code and ARM code.
The PRU code comes in the form of a binary module with the BeBoPr++ and

is proprietary. Yet, the PRU code is stored in the memory chip on the BeBoPr++. It is shipped together with the BeBoPr ++, so any lab that follows our part list and instructions will have the PRU code at no additional cost. The PRU code runs on the co-processors and controls the timing and acceleration for the stepper motors. The ARM code is open source and well commented. It forms a layer above the PRU code and is responsible for tasks like command parsing, G-code (MIT, Cambridge, MA, USA) processing, distance calculation, etc. This software works with command line interface and responds to G-code commands by user input. We forked the project from https://github.com/modmaker/BeBoPr and adapted it for COSI Measure. A graphical user interface (GUI, Fig. 3) was developed with PyQt (version 4.9.3)[54] to integrate all the functions, so that we could have a more user friendly interface than the command line interface. It provides four functions:
1) System initialization: Initialize the motor controller and the serial port, which connects to the measuring instrument (e.g. a Gaussmeter). A server was implemented in the motor controller ARM code. During system initialization the GUI starts the motor controller and establishes a link to the server so that the GUI can send commands to the motor controller and check its status. Two status indicators represent the status of the motor controller and the serial port respectively. A green indicator indicates the motor controller or the serial port functioning correctly, otherwise red. A sub-window shows the motor controller interface.
2) Homing: Move along the whole measurement range until x , y , z
and x | , y | and z | are found. An indicator will turn green when this
process is finished without error.
3) Single coordinate measurement: Move to a single point and read sensor data. The machine moves to a location specified by the user (coordinates are in millimeters, e.g. × 100y200z300) and then takes a measurement. The readout is then displayed on a sub-window of the GUI.
4) 2D/3D path measurement: Move and measure along a user defined trajectory. The user should provide two files in which one contains the trajectory (each line contains one coordinate in millimeters); the other will have the raw measurement results appended. A progress bar was implemented to show the measuring process.

Figure 3

min | min | min
max | max | max

Graphical user interface for COSI Measure. The left side of the GUI contains windows of the four functions: system initialization, homing, single coordinate measurement and 2D/3D path measurement. The top half of the right side of the GUI displays the status of the motor movements while the bottom half shows the measurement readouts.

The software project can be found under “software” directory in the project repository.

COSI Measure was evaluated for backlash, precision, speed and strength. In order to investigate the precision of the system and the reproducibility of the position after several iterations, a home-built 1 W 405 nm laser device attached to the probe holder was used to engrave dots on a piece of paper. The experiment setup and engraving process was recorded in Supplementary Video S1. For testing the precision of COSI Measure, the laser device was first moved along a trajectory with defined coordinate points (41 points along a straight line 0.5 mm apart) and with a 0.2 s stop at each point to engrave the paper. The laser device was then moved 10 iterations following the same pattern with a homing process inserted after the fifth iteration to fully test the backlash/reproducibility performance of the system. A series of concentric circles (7 circles with 1 mm radius increments starting from 1 mm, each circle has 12 evenly distributed points) were also programmed to further demonstrate the precision of the system. This experiment was repeated on x-y plane, x-z plane and y-z plane respectively for a thorough 3D evaluation. A digital calliper (resolution = 0.01 mm, Orion Tool, IL, USA), a ruler (resolution = 0.5 mm, Orion Tool, IL, USA) and a camera (EOS60D, Canon, Tokyo, Japan) were used to measure the distance between the engraved dots.

In order to measure the maximum load of the machine, a force meter (Samsonite, Luxembourg City, Luxembourg) was attached to the probe holder and hooked to the frame (Fig. 4a). COSI Measure was then moved vertically along the z-axis upwards. By reading the force meter at the point when COSI Measure could no longer move further, we could get its maximum load. A scale (Model: Pharo, Leifheit AG, Nassau, Lahn, Germany) was put under the probe holder (Fig. 4b) to test the maximum force. Similarly, we made the machine move vertically along the z-axis downwards; from the scale we can get the maximum force information. This parameter was examined in two scenarios: constrained (COSI Measure was fixed to the ground) and unconstrained. We also measured the time taken for the system to move along a single axis over a distance of 500 mm in order to get the speed of the system. Each measurement (load, force and speed) was repeated for 10 times to get an average result.

Figure 4
Experiment setup for testing force and load. (a) A force meter was attached to the probe holder and hooked to the frame to test the maximum load. It shows 21 kg when COSI Measure cannot move further. (b) A scale was put under the probe holder to test the maximum force. It is 55.1 kg when COSI Measure is unconstrained (not fixed to the ground).

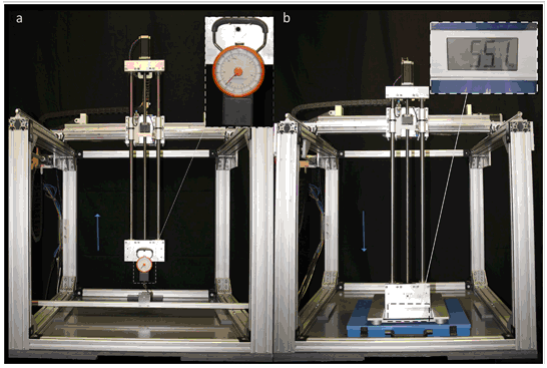
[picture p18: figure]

To demonstrate high fidelity automatic field mapping in a scientific application, a Gaussmeter (Model 460, Lake Shore Cryotronics, OH, USA) probe was positioned in a customized 3D printed probe holder (CAD files available) to map the magnetic field of a permanent magnet in a Halbach ring arrangement which will be used in the construction of a prototype magnet for an open source MRI scanner[19]. The experiment was partly recorded in Supplementary Video S2. The field mapping results were compared to magnetostatic field simulations (CST MWS 2015, Darmstadt, Germany) performed with the same Halbach ring configuration. COSI Measure moves along a 2D spiral trajectory (inside to outside) defined by an input path definition file. A slice in space with an area of (60 × 60) mm and a spatial resolution of 2 mm was covered in the mapping. After each coordinate COSI Measure interacts with the Gaussmeter and records the measured values of the 3-axis Hallprobe (MMZ-2508-UH, Lake Shore Cryotronics, OH, USA).

Stray magnetic field measurements were conducted for an actively shielded 3.0 T (Magnetom Verio, Siemens Medical, Erlangen, Germany) and a passively shielded 7.0 T (Magnetom, Siemens Medical, Erlangen, Germany) whole body MR scanner. Supplementary Video S3 depicts sequences of the measurement of the 3.0 T MR scanner. The magnetic field was measured with a 3-axis Hallprobe (MMZ-2508-UH, Lake Shore Cryotronics, OH, USA) in two (50 × 50) cm transverse planes at a 90 cm distance to the MRI scanner. The centre of the planes was aligned with the horizontal centre line of the MR

2

2

scanner bore. With a spatial resolution of 5 mm, 10201 (101 × 101) points were acquired in total for each plane. The Hallprobe was attached to an aluminium rod (length = 129 cm for 3.0 T, length = 255 cm for 7.0 T) which was attached to the probe holder of COSI Measure. A 3 seconds pause was programmed after each movement to reduce the vibration at the tip of the extension rod.

At last, the temperature distribution of an RF heating coil was examined. This shielded eight-rung highpass birdcage coil with an inner diameter of 20 cm was designed for scrutinizing RF power deposition induced heating[38]. A phantom (8 × 9 × 8 cm ) containing 650 ml fumed silica and water mixture (1 g: 5 g) was placed in the centre of the RF coil as an object under (heating) investigation. A signal generator (Model: SMGL, Rohde & Schwarz, Munich, Germany) and a power amplifier were used to drive the coil with an average output power of ~70 W at 297 MHz. A power meter (Model: NRT, Rohde & Schwarz, Munich, Germany) was inserted between the amplifier and the coil to monitor the power output. A fibre optic temperature sensor (Model: TC, Neoptix Inc, Québec City, Québec, Canada) attached to the probe holder of COSI Measure was used to capture the temperature profiles across the phantom after reaching the heating equilibrium (about 120 min). A fibre optic temperature monitor (OmniFlex, Neoptix Inc, Québec City, Québec, Canada) was connected to the sensor to log temperature data. The same RF power was applied to the RF coil during the mapping process to maintain the equilibrium. A (50 × 50) mm horizontal slice aligned with the centre of the RF coil was selected with a 1 mm spatial resolution. The mechanical subsystem of COSI Measure, the RF coil and the phantom were fixed inside the 7.0 T MR scanner room to take advantage of the shielding of the scanner room, so that the experiment would not generate electromagnetic interferences. Supplementary Video S4 illustrates the temperature measurement.

The data that support the findings of this study are available from www.opensourceimaging.org.

Figure 5 demonstrates the COSI Measure system measuring a home-built Halbach magnet. The maximum working volume of COSI Measure is (530 × 530 × 640) mm with a maximum moving speed of 37 mm/s. The maximum

3

2

3

load on the probe holder is 21 kg which makes the machine capable of supporting heavy scientific instruments and tools. While it is not fixed to the ground, the maximum force which the machine can apply to an object vertically downwards is 540.35 N (55.1 kg). This parameter increases to 896.33 N (91.4 kg) when COSI Measure is fixed to the ground.

Figure 5
COSI Measure, a low cost precise open source multipurpose measurement system. (a) personal computer chassis with electronic components inside (b) aluminium frame (c) motors (d) probe holder (e) Gaussmeter (f) Halbach ring magnets as object under investigation (g) cable chain holder (h) limit switch (i) movable lift table (j) emergency push button (k) Hall sensor probe ((e), (f) and
(k) are not part of COSI Measure, they are shown here for illustrating the measurement setup.)

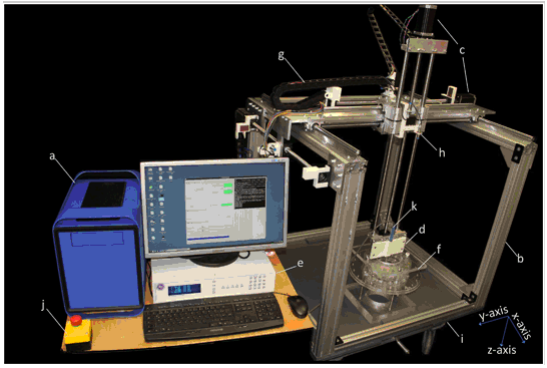
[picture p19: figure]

First, the spatial fidelity and reproducibility of COSI Measure was evaluated by laser engraving a computer defined dot pattern consisting of 41 points along a straight line 0.5 mm apart. Figure 6 illustrates the results of the precision and reproducibility measurements for the x-y plane. The upper line was engraved in one iteration along the y-axis and the lower line was burned into the paper in ten iterations including a homing process inserted after the fifth iteration. The average diameter of the points increased from 0.1 mm to 0.25 mm when they were engraved multiple times. The laser device returned to exactly the same location at the first point after each iteration. Even with the homing process inserted, no visible backlash was observed. A maximum deviation of 0.16 mm on the x-axis (perpendicular to the moving direction y-axis) was measured. Table 3 contains the detailed measurement results for the distance between two adjacent points for the experiment on x-y plane. The 7 concentric circles were in full accordance with the programmed trajectory definition and showed ample precision of the system with 2D movements. Experiments on x-z and y-z plane exhibited almost identical results. These results demonstrate the submillimetre precision and underline the reproducibility and backlash free performance of COSI Measure.

Figure 6
Precision and reproducibility results. (a) a 2 cent Euro coin, diameter 18.75mm
(b) the ruler, resolution = 0.5 mm (c) 7 concentric circles with 1 mm radius increments starting from 1 mm, each circle has 12 evenly distributed points (d) a straight line contains 41 points with 0.5 mm apart, engraved in one iteration
(d) a straight line contains 41 points with 0.5 mm apart, engraved in ten iterations.

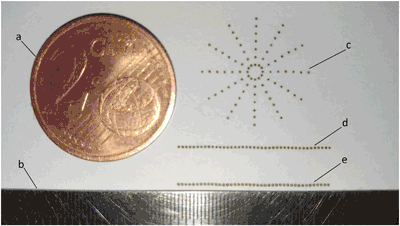
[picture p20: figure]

Table 3
Measurement results for the distance between two points on x-y plane (mm).
1 iteration | 0.50 | 0.47 | 0.52 | 0.08
10 iterations | 0.50 | 0.48 | 0.53 | 0.07

Next we replaced the laser device by an H-field sensor to examine the applicability of COSI Measure for the assessment of the magnetic field distribution of a single ring Halbach magnet with a diameter of 13.85 cm. These measurements are essential to benchmark the field uniformity against the field distribution deduced from magnetostatic field simulations which were undertaken during the design phase of the development process.
Figure 7a shows the measured in-plane magnetic flux density distribution of the Halbach magnet. For comparison the field dispersion deduced from the magnetostatic field simulation of the same Halbach magnet design is depicted in Fig. 7b. Figure 7c,d highlight the comparison between the measurements and simulation results for the same magnet through the magnet centre along y-and x-axis respectively. A maximum deviation of 1.9% was observed between simulated and measured magnetic flux density, which provides major encouragement for further development, simulation and implementation of novel Halbach magnet designs.

Figure 7
Magnetic flux density mapping results of a Halbach ring magnet compared with simulation results. (a) Measurement results of a 60 × 60 mm slice with the centre of the ring being the isocenter, the spatial mapping resolution was 2 mm.
(b) Simulation results with the same setup. (c) Comparison of the line plots through the isocenter between the measurement and simulation on the y-axis. A maximum deviation of 1.9% was observed. (d) Comparison between of the line plots through the isocenter the measurement and simulation on the x-axis. A maximum deviation of 1% was observed.

2

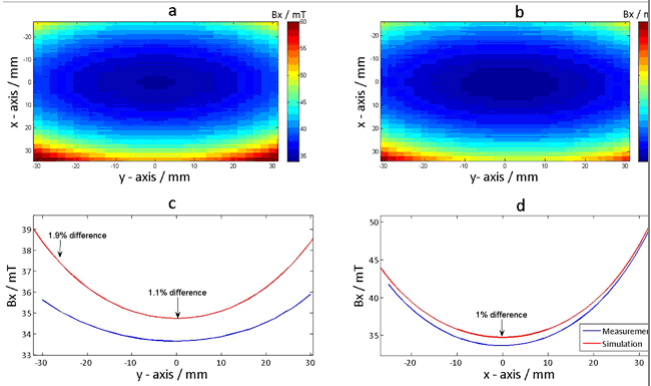
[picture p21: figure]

Next we extended the probe head by an aluminium rod and attached an H-field sensor horizontally to the tip of the rod. COSI Measure was positioned at the rear end of the patient table of a 3.0 T MR scanner and at the back side of a 7.0 T MR scanner to characterize the stray magnetic field strength and uniformity in an area close but aligned to the magnet bore. We consider this stray field to be used for MRI at low magnetic field strengths similar to that of the Halbach magnet. The vector magnitude derived from the stray field mapping of the 3.0 T and 7.0 T MRI scanners are summarized in Fig. 8c and
d. Positioning COSI Measure at the end of the patient table of the actively shielded 3.0 T system with a 129 cm rod supporting the H-field sensor did not affect its functionality and did not evoke too excessive attraction forces due to the stray field of the MRI system, which is approximately 2.5 mT at this position. For the passively shielded 7.0 T magnet the inductive limit switches started to malfunction at a distance of ~3 m away from the magnets rear end where the stray field was around 45 mT. Notwithstanding this minor malfunction the stray field could be successfully mapped using a longer aluminium rod with a length of 255 cm to accommodate and guide the H-field sensor. The measured fields for both the 3.0 T and the 7.0 T magnet show an expected maximum B in the centre of a plane perpendicular to the B direction. The smooth transitions in the field plot demonstrate that minor vibrations of the base system, which might be amplified over the length of the rod are small enough (<5 mm mapping resolution) to not disturb the measured
0 | z

data (Fig. 8c and d). Our measurements underline the excellent field uniformity of the stray field and make this stray field an ideal candidate for MRI in a low field environment of a commercial superconducting magnet to be used as a reference for our results obtained from a home-built low field permanent Halbach magnet.

Figure 8
Stray field mapping setup and results. (a) Stray field mapping setup in the 3 T scanner room, a 50 × 50 cm square transverse slice 90 cm outside the bore was selected. (b) Stray field mapping setup in the 7 T scanner room, a 50 × 50 cm square transverse slice 90 cm outside the bore (from the back side of the scanner) was selected. (c) Stray field mapping results (vector magnitude) of the selected slice for the 3 T scanner (spatial resolution: 5 mm). (d) Stray field mapping results (vector magnitude) of the selected slice for the 7 T scanner (spatial resolution: 5 mm).

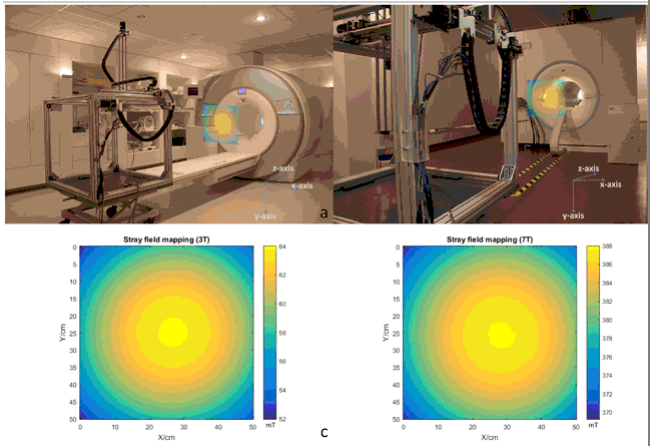
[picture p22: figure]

To take COSI Measure to the next application, a fibre optic temperature sensor was attached to the probe holder to capture the temperature profile across a phantom placed in the RF coil used for RF induced heating. The temperature distribution of the heated phantom is illustrated in Fig. 9. This 50 × 50 mm

2

temperature mapping has a spatial resolution of 1 mm. The map was acquired in ~100 min (2.4 s per point) right after the thermal equilibrium was achieved, which took 120 min with 70 W signal driving the coil and an initial phantom temperature of 21.9 °C. At the right side of the phantom, which is closer to the feeding point of the RF coil, higher temperatures are observed. The result indicates that COSI Measure is able to move smoothly not disturbing the temperature distribution in the object under investigation.

Figure 9
2D fibre optic temperature mapping result. Temperature mapping result after reaching the RF heating equilibrium of the silica/water phantom. A (50 × 50) mm horizontal slice aligned with the centre of the RF coil was selected and sampled with a 1 mm spatial resolution. Initially the phantom had a temperature of 21.9 °C.

An automated open source and versatile 3D measurement system (COSI Measure) was developed and validated. Our main findings are that COSI Measure supports a submillimetre spatial resolution that can be utilized for a broad range of measurements in MRI and related fields.

For the system design we ensured that all materials are easily accessible by the community. For example, the motors, proximity sensors and aluminium frames are standardized components which are made readily available by

2

numerous vendors. We customized COSI Measure in a way that it can be built and assembled conveniently. For example, instead of soldering a 44-pin CPLD chip onto the power management board, we chose to use a small and cheap CPLD development board plugged onto the power management board. Our goal was to make COSI Measure affordable. For example, we employed inexpensive yet accurate enough stepper motors and inductive proximity sensors. It is a strength of COSI Measure that it employs open source hardware and software whenever possible. The Beagle Bone Black is an open source design. The operating system (Linux) and the ARM motor control program are also open source. To ensure reproducibility of COSI Measure and our proof-of-principle experiments we provide a detailed part list, in-depth assembly instructions and detailed documentation of our experiments.

COSI Measure consists of 3-orthogonal axes with a working volume of (530 × 530 × 640) mm . It is open to all dimensions allowing for flexible measurement positioning. The experimental results demonstrated submillimetre spatial fidelity and reproducibility of the system and no significant backlash. COSI Measure is able to carry a load of up to 21 kg, which supports the attachment of a broad range of probe heads including temperature, ultrasound, optical, radiation and electromagnetic sensors and probe holders.

By equipping COSI Measure with a Halbach probe the capability for mapping magnetic fields was demonstrated using a Halbach magnet as an example. Our measurements detected an absolute deviation between magnetostatic field simulations and measurements of only 1.9%. In another example we illustrated the performance and utility of COSI Measure for mapping the stray magnetic field of an actively shielded clinical 3.0 T MRI scanner and of a passively shielded human 7.0 T MRI scanner. The strong magnetic stray field of the passively shielded 7.0 T set the limit of a distance of 3 m (~45 mT) for COSI Measure. At this field strength the inductive limit switches started to work outside of their specification. Changing the limit switches to mechanical configurations would address this malfunction. However, when positioning the base of COSI Measure into stronger magnetic fields magnetic forces of the magnet on the stepper motors become too large. This limitation can be relaxed by using extensions of the probe head. A rigid extension might magnify the vibration of the system but will not hamper the fidelity of COSI Measure. With an extended rigid probe holder in-bore measurements are feasible for 7.0 T, 3.0 T magnets and at lower magnetic field strengths. COSI Measure

3

would be even capable to support data sampling in the isocenter of a 9.4 T human MR scanner as long as a proper probe holder is provided. Arguably, extended probe heads increase the sensitivity of the measurement system to vibrations, which need to be accounted for by using decreased speed and/or longer waiting times for each measurement point. Using a probe holder with a length of 255 cm allowed successful mapping of the magnetic field in a plane located at a 90 cm distance from the rear end of a 7.0 T MR magnet. For this setup no extra infidelity was caused by vibration due to the use of a 3 s waiting time per measurement point.

COSI Measure is well suited for conducting RF antenna/coil characterization experiments by mapping the E-field, the H-field or the temperature as demonstrated by the temperature mapping results. This is of particular interest for explorations into thermal MR[35, 36, 37] and MR safety[38, 39, 40, 41, 44] where the measurements of RF induced temperatures might require submillimetre resolution. COSI Measure enables such measurements which are essential for designing new RF transmission antennae, for validating findings obtained from electromagnetic field simulations or for investigations into RF induced heating of electrically conductive implants. Admittedly, covering a 50 × 50 mm area for temperature mapping with a sampling rate of ~2.4 s per point consumed ~100 min in this study. This time can be reduced significantly for the experimental setup proposed here. Attaching an array of fibre optic sensors and reducing the sampling time per point would further accelerate data acquisition while maintaining the superb spatial resolution (1 mm).

The open-source nature, large working volume, robust configuration and high fidelity of COSI Measure make it not only suitable for advancing MR research but also for a variety of scenarios where accurate positioning and repeated movements are necessary. In millimetre-wave communication/radar systems, where antenna characteristics such as radiation pattern, reflection and scattering are important, a 3D test setup for characterization is usually required[55, 56, 57, 58, 59]. With minor modifications (e.g. adding an absorption cover), which can be conveniently accomplished since all the technical details of COSI Measure are freely accessible, COSI Measure can be easily turned into a 3D antenna test bench. Another possible application could be in durability/fatigue testing which usually involves cyclic movements and is common in aerospace, automotive, defence, manufacturing and electronic industries. COSI Measure already provides a robust setup, with extra

2

components added (e.g. a load cell); it can also be used as a fatigue testing system.

Further improvements of COSI Measure include automatic mapping of an object using distance sensors or a camera together with computer vision algorithms[60]. This would allow one to easily map the field of complex geometries such as RF coils, medical implants etc., which otherwise requires prior planning of the measurement path based on location and geometry of the object to measure. The moving speed of the machine could also be improved by further tuning the motor control algorithm. The observed maximum 0.16 mm deviation on the axis perpendicular to the moving direction was induced by the imperfection of the threaded shafts in the ball screws. This can be improved by replacing the shafts with more precise ones.

Parallel to the publication of this manuscript soft- and hardware of COSI Measure will be made available open source on www.opensourceimaging.org. Open source provides unique opportunities to modify and expand the capabilities of COSI Measure for a broader range of applications. With a downward force of >500 N (50 kg) mechanic tools such as a drill, saw or mill can be mounted to the probe holder. The submillimetre precision of the base system also affords 3D printing or SMD soldering. These applications are already supported by the hardware and hence would require only minor modifications in software along with setting up a dedicated holder tailored for the particular tool or probe head. In a resource limited research setting, such an approach allows for an efficient use of laboratory space, financial resources (both investment and maintenance) and collaborative efforts of the research community to extend the functionality. To summarize COSI Measure is in full alignment with the idea of open access for everybody and with the needs of reproducibility and rigour of research as requested by numerous authorities, the various funding bodies, the general public and the research communities.

Electronic supplementary material

Supplementary information accompanies this paper at https://doi.org/10.1038/s41598-017-13824-z.

Publisher's note: Springer Nature remains neutral with regard to jurisdictional claims in published maps and institutional affiliations.

We wish to acknowledge Steffen Tornow and Martin Pflaume for stimulating discussions on the mechanical setup and Felix Arndt for legal support and stimulating discussions around open source licensing. We further wish to acknowledge Yiyi Ji, Henning Matthias Reimann, Joao dos Santos Periquito, Laura Böhmert, Celal Öezerdem, Min-Chi Ku, Daniel Wenz, Sabrina Klix and Till Huelnhagen (Berlin Ultrahigh Field Facility (B.U.F.F.), Max Delbrüeck Center for Molecular Medicine, Berlin, Germany) for discussions, advice, technical and other assistance. This work was supported in part (LW, EO, HW, TN) by the Federal Ministry for Education and Research (BMBF, KMU innovativ Medizintechnik, 3-in-1 THERAHEAT, FKZ 13GW0102A and 13GW0102B).

Author Contributions
H.H., T.N. and L.W. wrote the manuscript. R.M. prepared Figure 7. H.H., T.N., E.O., H.W. and L.W. designed the experiments. All authors reviewed the manuscript.

Competing Interests Thoralf Niendorf is founder and CEO of MRI.TOOLS GmbH. Helmar Waiczies is employee of MRI.TOOLS GmbH.

Supplementary Video S1 Supplementary Video S2 Supplementary Video S3

Supplementary Video S4

1. Fuchs, V. R. & Sox, H. C. Jr Physicians’ views of the relative importance of thirty medical innovations. Health Aff (Millwood) 20, 30–42 (2001).
2. Mollura, D. J. & Lungren, M. P. Radiology in Global Health: Strategies, Implementation and Applications. (Springer, 2014).
3. Ambale-Venkatesh, B. & Lima, J. A. Cardiac MRI: a central prognostic tool in myocardial fibrosis. Nat Rev Cardiol 12, 18–29, https://doi.org/10.1038/nrcardio.2014.159 (2015).
4. Lerch, J. P. et al. Studying neuroanatomy using MRI. Nat. Neurosci. 20, 314–326, https://doi.org/10.1038/nn.4501 (2017).
5. Schepkin, V. D. et al. In vivo magnetic resonance imaging of sodium and diffusion in rat glioma at 21.1 T. Magn Reson Med 67, 1159–1166 (2012).
6. Hemmer, P. Toward molecular-scale MRI. Science 339, 1033–1033 (2013).
7. Brandejsky, V., Boesch, C. & Kreis, R. Proton Diffusion Tensor Spectroscopy of Metabolites in Human Muscle In Vivo. Magn Reson Med 73, 481–487 (2015).
8. Ludwig, U. et al. Dental MRI using wireless intraoral coils. Sci Rep 6, 23301, https://doi.org/10.1038/srep23301 (2016).
9. Itakura, H. et al. Magnetic resonance image features identify glioblastoma phenotypic subtypes with distinct molecular pathway activities. Sci Transl Med 7(303), 303ra138, https://doi.org/10.1126/scitranslmed.aaa7582 (2015).
10. Yu, X. et al. Sensory and optogenetically driven single-vessel fMRI. Nat Methods 13, 337–340 (2016).
11. Martel, S. Beyond imaging: Macro- and microscale medical robots actuated by clinical MRI scanners. Science Robotics 2, https://doi.org/10.1126/scirobotics.aam8119 (2017).
12. Tonelli, A. R. Estimation of Blood Flow Resistance in the Lung with MRI. Sci Transl Med 5, 200ec144, https://doi.org/10.1126/scitranslmed.3007308 (2013).
13. Graessl, A. et al. Sodium MRI of the human heart at 7.0 T: preliminary results. NMR Biomed 28, 967–975, https://doi.org/10.1002/nbm.3338 (2015).

14. Niendorf, T. et al. W(h)ither human cardiac and body magnetic resonance at ultrahigh fields? technical advances, practical considerations, applications, and clinical opportunities. NMR Biomed 29, 1173–1197, https://doi.org/10.1002/nbm.3268 (2016).
15. Waiczies, H. et al. Monitoring dendritic cell migration using 19F/1H magnetic resonance imaging. J Vis Exp, e50251, https://doi.org/10.3791/50251 (2013).
16. Niendorf, T. et al. High Field CardiacMagnetic Resonance Imaging: A Case for Ultrahigh Field Cardiac Magnetic Resonance. Circ Cardiovasc Imaging 10, https://doi.org/10.1161/CIRCIMAGING.116.005460 (2017).
17. Niendorf, T., Barth, M., Kober, F. & Trattnig, S. From ultrahigh to extreme field magnetic resonance: where physics, biology and medicine meet. MAGMA 29, 309–311, https://doi.org/10.1007/s10334-016-0564-1 (2016).
18. Cooley, C. Z. et al. Two-dimensional imaging in a lightweight portable MRI scanner without gradient coils. Magn Reson Med 73, 872–883, https://doi.org/10.1002/mrm.25147 (2015).
19. Winter, L., Barghoorn, A., Blümler, P. & Niendorf, T. COSI Magnet: Halbach Magnet and Halbach Gradient Designs for Open Source Low Cost MRI. In Proc Intl Soc Mag Reson Med 3568 (2016).
20. Blumler, P. Proposal for a permanent magnet system with a constant gradient mechanically adjustable in direction and strength. Concept Magn Reson B 46, 41–48 (2016).
21. Chronik, B. A., Alejski, A. & Rutt, B. K. Design and fabrication of a three-axis edge ROU head and neck gradient coil. Magn Reson Med 44, 955–963 (2000).
22. Turner, R. Gradient Coil Design - a Review of Methods. Magn Reson Imaging 11, 903–920 (1993).
23. Winter, L. et al. Comparison of three multichannel transmit/receive radiofrequency coil configurations for anatomic and functional cardiac MRI at 7.0T: implications for clinical imaging. Eur Radiol 22, 2211–2220

(2012).

24. Raaijmakers, A. J. E. et al. The fractionated dipole antenna: A new antenna for body imaging at 7 Tesla. Magn Reson Med 75, 1366–1374 (2016).
25. Adriany, G. et al. A geometrically adjustable 16-channel transmit/receive transmission line array for improved RF efficiency and parallel imaging performance at 7 Tesla. Magn Reson Med 59, 590–597 (2008).
26. Brunner, D. O., De Zanche, N., Frohlich, J., Paska, J. & Pruessmann,
K. P. Travelling-wave nuclear magnetic resonance. Nature 457, 994–U992 (2009).
27. Graessl, A. et al. Modular 32-channel transceiver coil array for cardiac MRI at 7.0T. Magn Reson Med 72, 276–290, https://doi.org/10.1002/mrm.24903 (2014).
28. Oezerdem, C. et al. 16-channel bow tie antenna transceiver array for cardiac MR at 7.0 tesla. Magn Reson Med 75, 2553–2565, https://doi.org/10.1002/mrm.25840 (2016).
29. Winter, L. & Niendorf, T. Electrodynamics and radiofrequency antenna concepts for human magnetic resonance at 23.5 T (1 GHz) and beyond. MAGMA 29, 641–656, https://doi.org/10.1007/s10334-016-0559-y (2016).
30. Stockmann, J. P. et al. A 32-channel combined RF and B0 shim array for 3T brain imaging. Magn Reson Med 75, 441–451, https://doi.org/10.1002/mrm.25587 (2016).
31. Kim, D. H., Adalsteinsson, E., Glover, G. H. & Spielman, D. M. Regularized higher-order in vivo shimming. Magn Reson Med 48, 715–722, https://doi.org/10.1002/mrm.10267 (2002).
32. Lutti, A. et al. Robust and fast whole brain mapping of the RF transmit field B1 at 7T. PLoS One 7, e32379, https://doi.org/10.1371/journal.pone.0032379 (2012).

33. Webb, A. G. & de Moortele, V. P. F. The technological future of 7 T MRI hardware. NMR Biomed 29, 1305–1315, https://doi.org/10.1002/nbm.3315 (2016).
34. Balidemaj, E. et al. In vivo electric conductivity of cervical cancer patients based on B(1)(+) maps at 3T MRI. Phys Med Biol 61, 1596–1607, https://doi.org/10.1088/0031-9155/61/4/1596 (2016).
35. Winter, L. et al. Thermal magnetic resonance: physics considerations and electromagnetic field simulations up to 23.5 Tesla (1 GHz). Radiat Oncol 10, 201, https://doi.org/10.1186/s13014-015-0510-9 (2015).
36. Tarasek, M. R. et al. Validation of MR thermometry: Method for temperature probe sensor registration accuracy in head and neck phantoms. Int J Hyperther 30, 142–149 (2014).
37. Winter, L. et al. Design and Evaluation of a Hybrid Radiofrequency Applicator for Magnetic Resonance Imaging and RF Induced Hyperthermia: Electromagnetic Field Simulations up to 14.0 Tesla and Proof-of-Concept at 7.0 Tesla. Plos One 8(4), e61661, https://doi.org/10.1371/journal.pone.0061661.
38. Santoro, D. et al. Detailing Radio Frequency Heating Induced by Coronary Stents: A 7.0 Tesla Magnetic Resonance Study. Plos One 7(11), e49963, https://doi.org/10.1371/journal.pone.0049963.
39. Winter, L. et al. On the RF Heating of Coronary Stents at 7.0 Tesla MRI. Magn Reson Med 74, 999–1010 (2015).
40. Neufeld, E., Kuhn, S., Szekely, G. & Kuster, N. Measurement, simulation and uncertainty assessment of implant heating during MRI. Phys Med Biol 54, 4151–4169 (2009).
41. Noureddine, Y. et al. In vitro and in silico assessment of RF-induced heating around intracranial aneurysm clips at 7 Tesla. Magn Reson Med, https://doi.org/10.1002/mrm.26650 (2017).
42. Eryaman, Y. et al. Radiofrequency heating studies on anesthetized swine using fractionated dipole antennas at 10.5 T. Magn Reson Med, https://doi.org/10.1002/mrm.26688 (2017).

43. Vavoulas, A. et al. Using a modified 3D-printer for mapping the magnetic field of RF coils designed for fetal and neonatal imaging. J Magn Reson 269, 146–151 (2016).
44. Oberacker, E. et al. Magnetic resonance safety and compatibility of tantalum markers used in proton beam therapy for intraocular tumors: A 7.0 Tesla study. Magn Reson Med, https://doi.org/10.1002/mrm.26534 (2016).
45. Gebhardt, P. et al. FPGA-based RF interference reduction techniques for simultaneous PET-MRI. Phys Med Biol 61, 3500– + (2016).
46. Winter, L. et al. Open Source Imaging Initiative. In Proc Intl Soc Mag Reson Med 3638 (2016).
47. Arndt, F. et al. Open Source Imaging Initiative (OSI²) – Update and Roadmap. In Proc Intl Soc Mag Reson Med 193 (2017).
48. Broche L, Pellicer-Guridi R, Winter L The Value of Open Source for Research, Education andGlobal Health - The Open Source Imaging Initiative. In Proc ESMRB (2017).
49. Prusa Research s.r.o. PRUSA i3 MK2S, http://www.prusa3d.com (2017).
50. Aleph Objects Inc. LulzBot TAZ 6, http://www.lulzbot.com (2017).
51. Jones, R. et al. RepRap - the replicating rapid prototyper. Robotica 29, 177–191, https://doi.org/10.1017/S026357471000069x (2011).
52. Negrier, A. Arduino Controlled CNC / 3D Printer Hybrid, http://www.instructables.com/id/Arduino-Controlled-CNC-3D-Printer/(2014).
53. The BeagleBoard.org Foundation. BeagleBone Black, https://beagleboard.org/black (2016).
54. Riverbank Computing Limited. What is PyQt, https://riverbankcomputing.com/software/pyqt/intro (2016).

55. Nashashibi, A. Y., Sarabandi, K., Al-Zaid, F. A. & Alhumaidi, S. Characterization of Radar Backscatter Response of Sand-Covered Surfaces at Millimeter-Wave Frequencies. IEEE Trans Geosci Remote Sens 50, 2345–2354 (2012).
56. Ranvier, S. et al. Compact 3-D on-Wafer Radiation Pattern Measurement System for 60 Ghz Antennas. Microw. Opt. Technol. Lett. 51, 319–324 (2009).
57. Fu, Y. Development of a test bench for characterization of integrated antennas at millimeter-wave frequencies, Université de Grenoble, (2012).
58. Titz, D. et al. Design and measurement of a dipole-antenna on a 130nm CMOS substrate for 60GHz communications. in 2010 Conference Proceedings ICECom 1–4.
59. Titz, D. et al. Measurement setup and associated calibration methodology for 3D radiation pattern of probe-fed millimeter-wave antennas. In 2011 Conference Proceedings LAPC 1–5.
60. Szeliski, R. Computer Vision: Algorithms and Applications. (Springer, 2011).

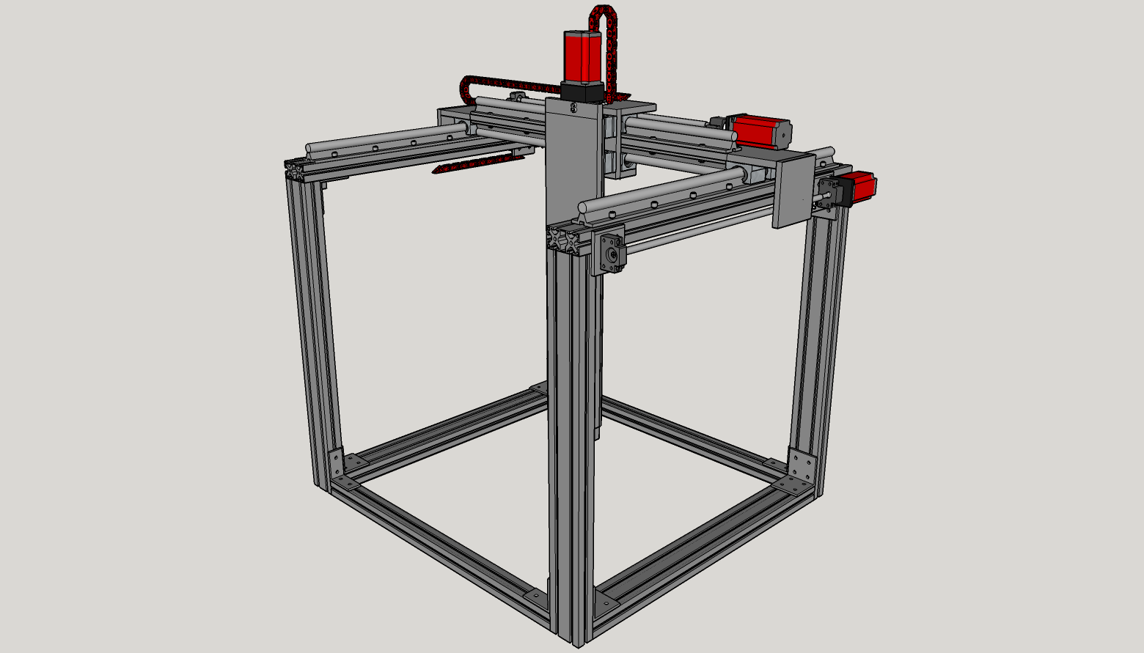
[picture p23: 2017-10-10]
Mechanical System/Complete System/design_in_png/complete_system_isometric.png

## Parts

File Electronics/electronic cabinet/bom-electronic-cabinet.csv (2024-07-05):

Position | Description | Designator | Qty | Manufacturer | Manufacturer PartNo | Distributor | Comment | Link
1 | Enclosure | - | 1 | Schneider Electric | NSYS3D6420P | reichelt |  | https://www.reichelt.de/stahlgehaeuse-s3d-mit-montageplatte-600-x-400-x-200-ip66-nsys3d6420p-p310670.html
2 | DIN Rails | - | 2 |  | 3575ZG-1M | reichelt |  | https://www.reichelt.de/at/de/hutschiene-35-x-7-5-mm-gelocht-1-m-hs-35x7-5-1m-p295662.html
3 | Cage Clamp bl | X1 | 5 | WAGO | 280-904 | reichelt |  | https://www.reichelt.de/at/de/durchgangsklemme-2-leiter-1-pol-0-08-2-5-mm-wago-280-904-p32237.html
4 | Cage Clamp gn-yl | X1 | 5 | WAGO | 280-907 | reichelt |  | https://www.reichelt.de/at/de/hutschiene-35-x-7-5-mm-gelocht-1-m-hs-35x7-5-1m-p295662.html
5 | Cage Clamp gy | X1 | 53 | WAGO | 280-901 | reichelt |  | https://www.reichelt.de/at/de/durchgangsklemme-2-leiter-1-pol-0-08-2-5-mm-wago-280-901-p32236.html
6 | Terminal Block Endcap | X1 | 1 | WAGO | 280-308 | reichelt |  | https://www.reichelt.de/at/de/abschluss-und-zwischenplatte-wago-280-308-p248633.html
7 | Terminal Block Bridges | X1 | 20 | WAGO | 280-402 | farnell |  | https://de.farnell.com/wago/280-402/querbr-cker-isoliert-grau/dp/1283454?MER=sy-me-pd-mi-acce
8 | Cable Duct 60x25 | - | 1 | arnocanali | V6K6025 | reichelt |  | https://www.reichelt.de/verdrahtungskanal-60x25-mm-1000-mm-v6k6025-p338230.html
9 | Cable Duct 60x40 | - | 1 | arnocanali | V6K6040 | reichelt |  | https://www.reichelt.de/verdrahtungskanal-60x40-mm-1000-mm-v6k6040-p275692.html
10 | Mounting Plate for Rumba and Pi | -
11 | Cable Tube | - | 1 | Rittal | 2595.000 | Conrad |  | https://www.conrad.de/de/p/rittal-sz-2595-000-kabelschlauch-polyethylen-o-x-l-16-mm-x-25-m-1-st-1048519.html
12 | Cable Tube Holder | - | 1 | Rittal | 2593.000 | Conrad |  | https://www.conrad.de/de/p/rittal-sz-2593-000-kabelschlauchhalter-polyamid-20-st-1048517.html
13 | Stepper Motor Driver |  | 3 | ACT | DM542 | reichelt |  | https://www.reichelt.de/schrittmotortreiber-fuer-nema-23-18-50-v-act-dm542-p237924.html
14 | Main Switch | S0 | 1 |  |  | reichelt |  | https://www.reichelt.de/hauptschalter-3-pol-25-a-eaton-041097-p158862.html
15 | Mains In | X0 | 1 | Deltron | RID1042H | rs |  | https://de.rs-online.com/web/p/iec-filter/7615775
16 | Power Socket | X2 | 1 | Schneider Electric | PKS52B | Conrad |  | https://www.conrad.de/de/p/schneider-electric-pks52b-einbau-steckdose-ip54-ik08-blau-2359161.html
17 | USB Through-Connector | X8, X9, X10 | 3 | CLIFF | CP30210NMB | reichelt |  | https://www.reichelt.de/sg/de/usb-adapter-ft-1-x-usb-3-0-a-buchse-1-x-usb-3-0-b-buchse-cliff-cp30210nmb-p227661.html
18 | HDMI Through-Connector | X11 | 1 | Delock | 86963 | reichelt |  | https://www.reichelt.de/sg/de/hdmi-a-einbaubuchse-mit-verschlusskappe-ip67-delock-86963-p322711.html
19 | RJ45 Through Connector | X12 | 1 | TRU Components | 4016139055312 | Conrad |  | https://www.conrad.de/de/p/tru-components-rj45-01-rj45-einbaubuchse-1408770-buchse-einbau-stecker-gerade-polzahl-8p8c-silber-1-st-1408770.html
20 | 3 pin ext. Emergency Stop Connector | X8 | 1 | binder | 99-0608-00-03 | Conrad |  | https://www.conrad.de/de/p/binder-99-0608-00-03-rundstecker-flanschstecker-gesamtpolzahl-3-serie-rundsteckverbinder-678-1-st-738745.html
21 | 8 pin Hardware Limit Switches | X3 | 1 | binder | 99-0648-00-08 | Conrad | see Issues! | https://www.conrad.de/de/p/binder-99-0648-00-08-rundstecker-flanschstecker-gesamtpolzahl-8-serie-rundsteckverbinder-678-1-st-738809.html
22 | 8 pin connector Endstops | X4 | 1 | binder | 99-0648-00-08 | Conrad | see Issues! | https://www.conrad.de/de/p/binder-99-0648-00-08-rundstecker-flanschstecker-gesamtpolzahl-8-serie-rundsteckverbinder-678-1-st-738809.html
23 | 6 pin Motor X-Axis Connector | X5 | 1 | binder | 99-000-06 | Conrad | see Issues! | https://www.conrad.de/de/p/binder-99-000-06-rundstecker-flanschstecker-gesamtpolzahl-6-serie-rundsteckverbinder-678-1-st-738783.html
24 | 6 pin Motor Y-Axis Connector | X6 | 1 | binder | 99-000-06 | Conrad | see Issues! | https://www.conrad.de/de/p/binder-99-000-06-rundstecker-flanschstecker-gesamtpolzahl-6-serie-rundsteckverbinder-678-1-st-738783.html
25 | 6 pin Motor Z-Axis Connector | X7 | 1 | binder | 99-000-06 | Conrad | see Issues! | https://www.conrad.de/de/p/binder-99-000-06-rundstecker-flanschstecker-gesamtpolzahl-6-serie-rundsteckverbinder-678-1-st-738783.html
26 | 24 V Power Supply | T1 | 1 | MEANWELL | NDR-480-24 | reichelt |  | https://www.reichelt.de/at/de/schaltnetzteil-hutschiene-480-w-24-v-20-a-mw-ndr-480-24-p264962.html
27 | 5 V PowerSupply | T2 | 1 | Siemens | 6EP3310-6SB00-0AY0 | reichelt | too expensive | https://www.reichelt.de/at/de/hutschienen-netzteil-5-v-3-a-logo-power-5v3-p348706.html
28 | Circuitbreaker, RCD | F1 | 1 | Schneider Electric | R9D01613 | reichelt | often not necessary | https://www.reichelt.de/at/de/fi-ls-schalter-resi9-1p-n-13a-b-char-30ma-typ-a-6ka-r9d01613-p292098.html
29 | Contactor DC3 | Q1 | 1 | Schneider Electric | LC1D12BD | reichelt | https://ckm-content.se.com/ckmContent/sfc/servlet.shepherd/document/download/0691H000008h5vrQAA | https://www.reichelt.de/at/de/leistungsschuetz-tesys-d-1-nc-3-1-no-5-5-kw-12-a-lc1d12bd-p211755.html
30 | Safety Relais | K1 | 1 | Schneider Electric | XPS-AC | obsolete | obsolet, replacement needed. See Issue | https://www.se.com/de/de/product/XPSAC5121/sicherheitsbaustein-nothalt-3-relais+1-transistor-24-vac-dc-fest/
31 | RaspberryPi | K2 | 1 | Raspberry Pi | RP-4B-8GB | Conrad |  | https://www.conrad.de/de/p/raspberry-pi-4-b-8-gb-4-x-1-5-ghz-raspberry-pi-2250399.html
32 | Rumba32 | K3 | 1 |  |  |  | modification needed see [here](Rumba32/README.md)
33 | Endstop BreakoutBoard | - | 1 |  |  |  | Rumba32/Driver_Breakoutboard/README.md
34 | Driver BreakoutBoard | - | 3 |  |  |  | Rumba32/Endstop_Levelshifter/README.md
35 | On-Off Switch | S4 | 1 | Eaton | M22-DDL-GR | Conrad |  | https://www.conrad.de/de/p/eaton-216509-m22-ddl-gr-x1-x0-k11-230-w-doppeldrucktaster-1-x-aus-ein-tastend-ip66-1-st-2306911.html
36 | Light for S4 (24V) | H1 | 1 | Eaton | 216557 | Conrad |  | https://www.conrad.de/de/p/eaton-m22-led-w-led-element-weiss-30-v-dc-ac-1-st-700321.html
37 | Emergency Stop | S2 | 1 | Eaton | 110938 | Conrad |  | https://www.conrad.de/de/p/eaton-m22-pv-k01-bvp-not-aus-schalter-1-oeffner-ip66-1-st-2132759.html
38 | USB-C Cable | - | 1 | hama | 201594 | Conrad |  | https://www.conrad.de/de/p/hama-usb-ladekabel-usb-2-0-usb-a-stecker-usb-c-stecker-1-00-m-schwarz-00201594-2886437.html
39 | USB A-B Cable | - | 3 | Delock | 82580 | Conrad |  | https://www.conrad.de/de/p/delock-usb-kabel-usb-3-2-gen1-usb-3-0-usb-3-1-gen1-usb-a-stecker-usb-b-stecker-1-00-m-blau-vergoldete-steckkontakte-1880889.html
40 | HDMI Cable | - | 1 | Digitus | AK-330115-010-S | Conrad |  | https://www.conrad.de/de/p/digitus-hdmi-anschlusskabel-hdmi-a-stecker-hdmi-micro-d-stecker-1-00-m-schwarz-ak-330115-010-s-vergoldete-steckkontakte-678202.html
41 | Micro USB-Cable | - | 1 | renkforce | RF-4316220 | Conrad |  | https://www.conrad.de/de/p/renkforce-usb-kabel-usb-2-0-usb-a-stecker-usb-micro-b-stecker-1-00-m-schwarz-vergoldete-steckkontakte-rf-4316220-1438740.html
42 | Jumper Cables | - | 1 | Joy-IT | RB-CB-025 | reichelt |  | https://www.reichelt.com/entwicklerboards-steckbrueckenkabel-25cm-20-kabel-debo-kabelset-p161046.html

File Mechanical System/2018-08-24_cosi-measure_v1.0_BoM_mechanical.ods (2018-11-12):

Number | Item | Description | Price | Pcs | Total Price | Links
1 | Aluminum frame | 40x80L I-Typ Nut 8, 80cm | 17,2 | 6 | 103,2 | https://www.dold-mechatronik.de/Aluminiumprofil-40x80L-I-Typ-Nut-8-Standardlaengen-215-EUR-m
2 | Angle | 40x80 l-Typ Nut 8 + screws | 4,66 | 16 | 74,56 | https://www.dold-mechatronik.de/Winkel-40x80-I-Typ-Nut-8-inkl-Befestigungssatz
3 | Aluminum frame | 40x40L I-Typ Nut 8, 80cm | 8,2 | 3 | 24,6 | https://www.dold-mechatronik.de/Aluminiumprofil-40x40L-I-Typ-Nut-8-Standardlaengen-1025-EUR-m
4 | Angle | 40 I-Typ Nut 8 + screws | 2,52 | 12 | 30,24 | https://www.dold-mechatronik.de/Stahlwinkel-40-I-Typ-Nut-8-inkl-Befestigungssatz
5 | Aluminum frame | 40x80L I-Typ Nut 8, 88cm | 19,66 | 2 | 39,32 | https://www.dold-mechatronik.de/Aluminiumprofil-40x80L-I-Typ-Nut-8-ZUSCHNITT-bis-1200-mm-2200-EUR-m-030-EUR-pro-Schnitt
5 | Slot nut | I-Typ Nut8, M8 | 0,53 | 10 | 5,3 | https://www.dold-mechatronik.de/Nutenstein-mit-Steg-I-Typ-Nut-8-Gewindedurchmesser-waehlbar
6 | Aluminum plate | AlCuMg1, EN AW-2017A.EN AW-AlCu4MgSi(A), T451 EN 485-1.2.3 | 184,45 | 1 | 184,45 | www.gemmel-metalle.de
7 | Screws | DIN7991-M8x20, countersunk | 0,3 | 10 | 3 | https://www.dold-mechatronik.de/DIN-7991-Senkschraube-mit-Innensechskant-88-verzinkt
8 | Slot nut | I-Typ Nut8, M5 | 0,53 | 24 | 12,72 | https://www.dold-mechatronik.de/Nutenstein-mit-Steg-I-Typ-Nut-8-Gewindedurchmesser-waehlbar
9 | Supported Rail | TBS20 rail 800mm | 33 | 4 | 132 | https://www.dold-mechatronik.de/Linearfuehrung-Supported-Rail-TBS20-800mm-lang
10 | Screw | DIN912-M5x20 | 0,13 | 32 | 4,16 | https://www.dold-mechatronik.de/DIN-912-Zylinderschraube-mit-Innensechskant-88-verzinkt
11 | Linear bearing | TBR20UU | 9,8 | 8 | 78,4 | https://www.dold-mechatronik.de/Linearlager-20mm-TBR20UU-offen-Spiel-einstellbar
12 | Ballscrew + spindle nut block | SFU1605-DM 652mm | 95 | 2 | 190 | https://www.dold-mechatronik.de/SET-Kugelumlaufspindel-SFU1605-DM-642mm-mit-Spindelmutterblock-fuer-Easy-Mechatronics-System-1620A-L600
13 | Fixed bearing + motor holder | FLB20-3200 fixed bearing and NEMA23 Motorholder | 53,9 | 2 | 107,8 | https://www.dold-mechatronik.de/Festlagereinheit-FLB20-3200-inkl-Motorhalter-NEMA23-Easy-Mechatronics-System-1620B
14 | Floating Bearing | LLB20-6200 floating bearing | 14,9 | 2 | 29,8 | https://www.dold-mechatronik.de/Loslagereinheit-LLB20-6200-Easy-Mechatronics-System-1620B
15 | Motor coupler | D25L30 8/8 | 10,5 | 2 | 21 | https://www.dold-mechatronik.de/Wellenkupplung-XB-flexibel-D25L30-800-800mm
16 | Easy-Mechatronics System | Linear axis configuration: 1x fixed bearing and motor holder NEMA23, 1x floating bearing, 4x linear bearings SCJ20UU, 2x präzisionshaft 20mm h6 840mm, 4x shaftholder SH20, 1x ballscrew with spindle nut block SFU1605-DM 852mm, 1x shaft coupling 8/8mm D25L30 | 271,3 | 1 | 271,3 | https://www.dold-mechatronik.de/Linearachse-Konfigurator-Easy-Mechatronics-System-1620B
17 | Screw | DIN912-M6x20 | 0,14 | 50 | 7 | https://www.dold-mechatronik.de/DIN-912-Zylinderschraube-mit-Innensechskant-88-verzinkt
18 | Screw | DIN7991-M6x20, countersunk | 0,3 | 16 | 4,8 | https://www.dold-mechatronik.de/DIN-7991-Senkschraube-mit-Innensechskant-88-verzinkt-M6x20
19 | Bolt | DIN912-M5x30 | 0,17 | 20 | 3,4 | https://www.dold-mechatronik.de/DIN-912-Zylinderschraube-mit-Innensechskant-88-verzinkt
20 | Screw | DIN7991-M5x20, countersunk | 0,3 | 4 | 1,2 | https://www.dold-mechatronik.de/DIN-7991-Senkschraube-mit-Innensechskant-88-verzinkt-M6x20
21 | Hexagon nut | DIN934-M5 | 0,15 | 24 | 3,6 | https://www.dold-mechatronik.de/DIN-934-Sechskantmutter-8-verzinkt
22 | distance holder | 1mm for TBR20UU linear bearing | 1,5 | 4 | 6 | https://www.dold-mechatronik.de/Distanzblech-1mm-fuer-TBR20UU
23 | distance holder | 1mm for ballscrew block | 1,5 | 2 | 3 | https://www.dold-mechatronik.de/Distanzblech-1mm-fuer-TR-Muttern-mit-Gehaeuse-16x4-und-16x8-sowie-Spindelmuttergehaeuse-HSFU1605
24 | Bolt | DIN912-M6x30 | 0,18 | 2 | 0,36 | https://www.dold-mechatronik.de/DIN-912-Zylinderschraube-mit-Innensechskant-88-verzinkt
25 | Screw nut | DIN934-M6 | 0,16 | 2 | 0,32 | https://www.dold-mechatronik.de/DIN-934-Sechskantmutter-8-verzinkt-M6x1
26 | cable mount |  | 1,11 | 4 | 4,44 | https://www.conrad.de/de/hellermanntyton-151-28469-mb4a-pa66-na-c1-befestigungssockel-selbstklebend-schraubbar-4fach-einfaedeln-halogenfrei-uv-541796.html
 |  | Total cost mechanical subsystem: | 1340,85

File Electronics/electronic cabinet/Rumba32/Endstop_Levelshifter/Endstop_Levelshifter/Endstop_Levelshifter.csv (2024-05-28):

Id | Designator | Package | Quantity | Designation | Supplier and ref
1 | J1 | 691210910008 | 1 | Conn_01x08
2 | C1 | C_0805_2012Metric_Pad1.18x1.45mm_HandSolder | 1 | 10n
3 | J4 | PinHeader_1x02_P2.54mm_Horizontal | 1 | Conn_01x02
4 | J3 | PinSocket_1x03_P2.54mm_Vertical | 1 | Conn_01x03
5 | J2 | PinSocket_1x05_P2.54mm_Vertical | 1 | Conn_01x05
6 | IC1 | TSSOP-16_4.4x5mm_P0.65mm | 1 | 74HC4050PW,118

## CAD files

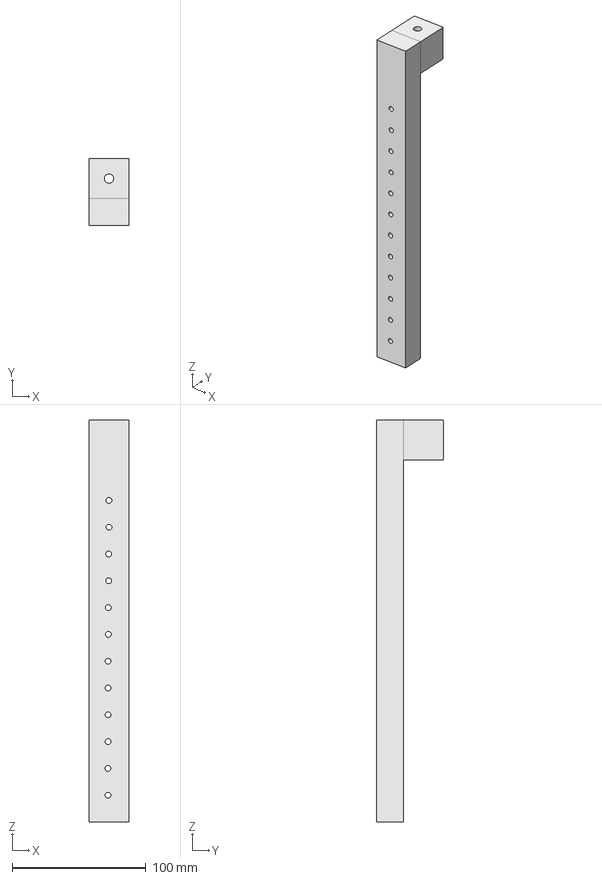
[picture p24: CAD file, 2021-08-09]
Accessoires/Lakeshore 460 Gaussmeter probe holder/Holder_Lakeshore_3-axis_withRod.step
30.0 x 50.0 x 300.0 mm

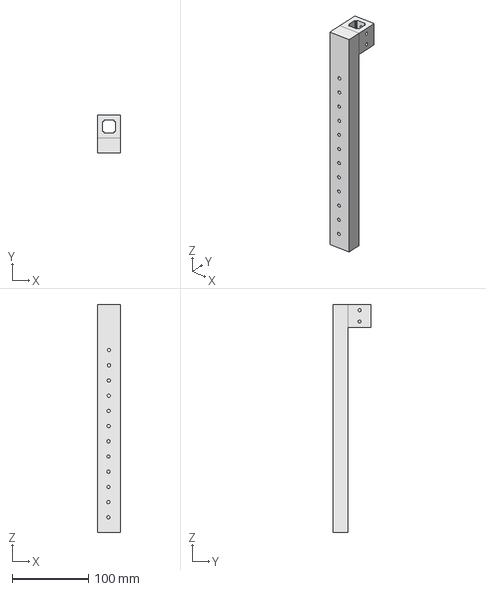
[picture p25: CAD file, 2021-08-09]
Accessoires/Metrolabs PT2026 probe holder/Holder_NMR_Probe_withRod.step
30.0 x 50.0 x 300.0 mm

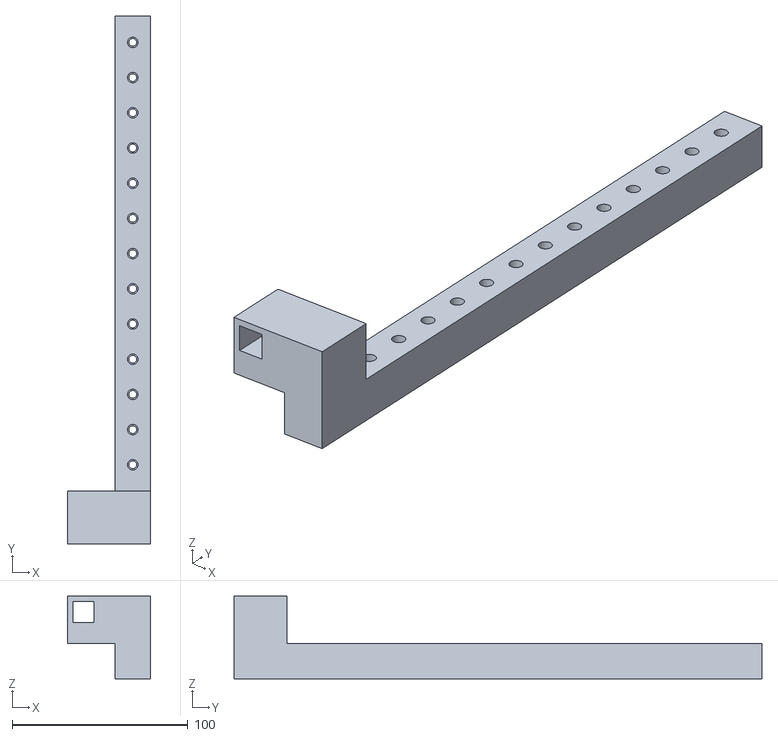
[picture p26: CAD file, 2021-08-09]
Accessoires/SPEAG H1TDS probe holder/H-field_holder_withRod_2.stl
47.0 x 300.0 x 47.0

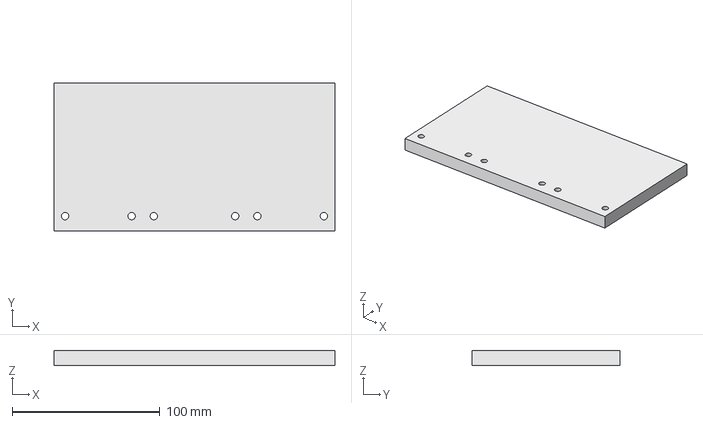
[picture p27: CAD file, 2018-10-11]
Mechanical System/Aluplates/FreeCAD/plate9.FCStd
190.0 x 100.0 x 10.0 mm

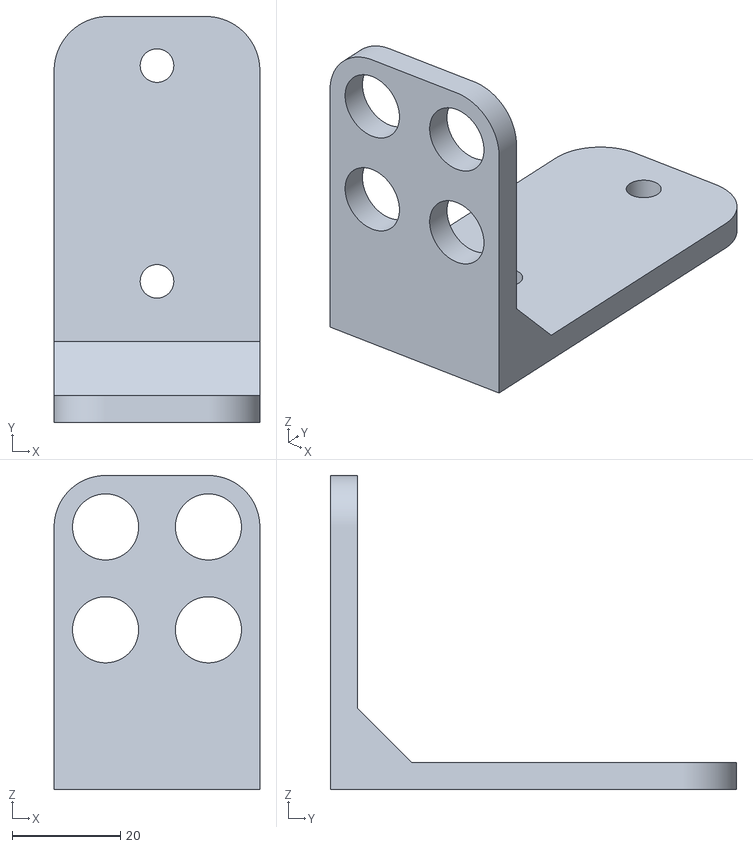
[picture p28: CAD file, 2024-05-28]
Mechanical System/Limit Switch Holder/Sensor Winkel1.stl
38.0 x 75.0 x 58.0

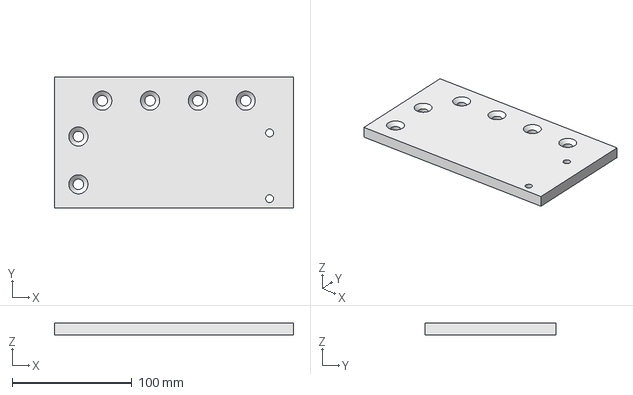
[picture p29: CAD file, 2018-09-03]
Mechanical System/Aluplates/FreeCAD/plate4.FCStd
200.0 x 110.0 x 10.0 mm

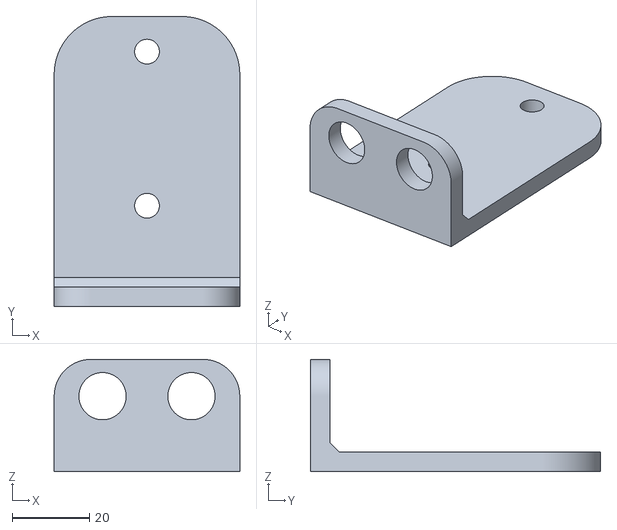
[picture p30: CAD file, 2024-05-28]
Mechanical System/Limit Switch Holder/Sensor Winkel1_kurz_lang.stl
48.0 x 75.0 x 29.0

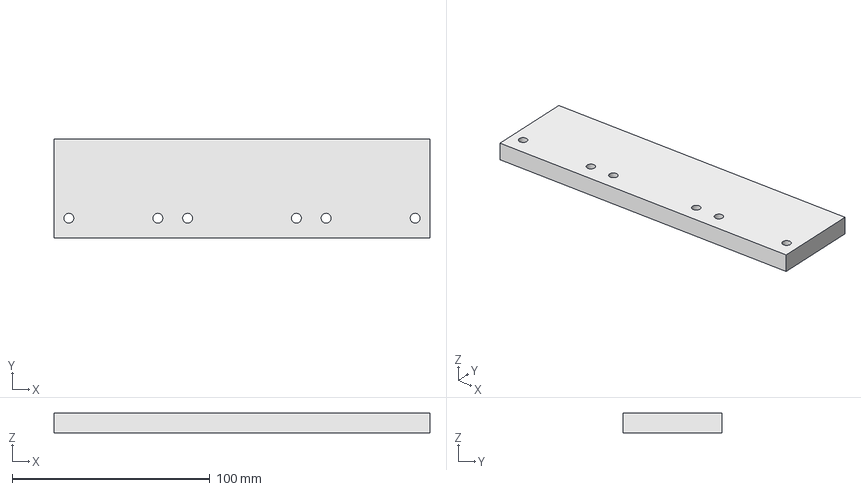
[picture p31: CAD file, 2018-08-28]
Mechanical System/Aluplates/FreeCAD/plate8.FCStd
190.0 x 50.0 x 10.0 mm

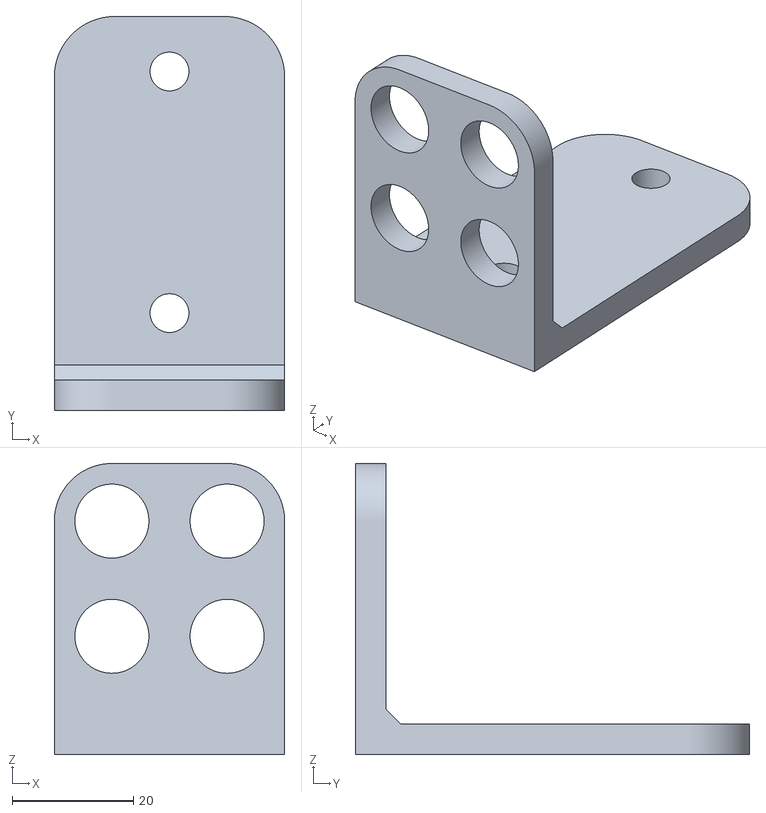
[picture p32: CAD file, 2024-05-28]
Mechanical System/Limit Switch Holder/Sensor Winkel1_kurz.stl
38.0 x 65.0 x 48.0

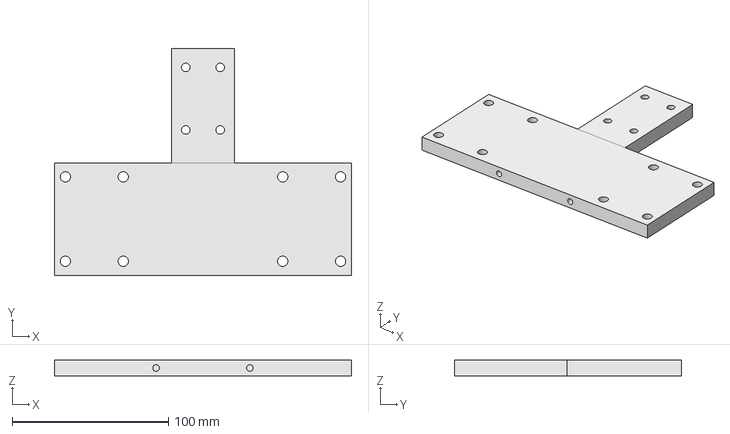
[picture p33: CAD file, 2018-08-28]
Mechanical System/Aluplates/FreeCAD/plate5.FCStd
190.0 x 145.0 x 10.0 mm

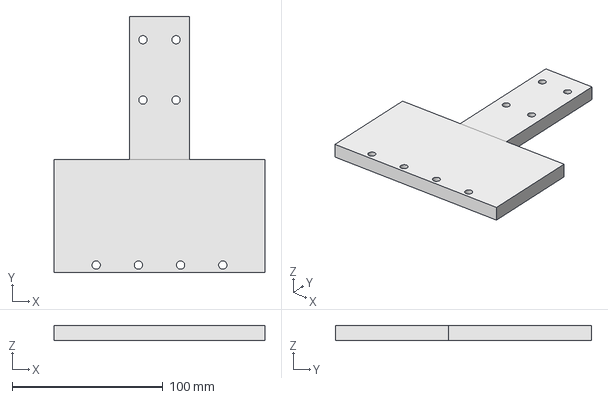
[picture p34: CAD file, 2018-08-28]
Mechanical System/Aluplates/FreeCAD/plate2.FCStd
140.0 x 170.0 x 10.0 mm

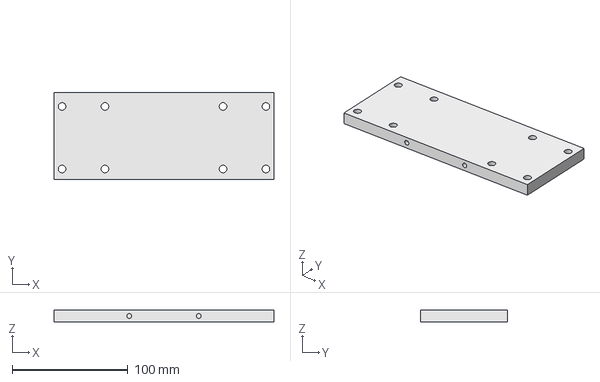
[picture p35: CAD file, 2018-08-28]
Mechanical System/Aluplates/FreeCAD/plate7.FCStd
190.0 x 75.0 x 10.0 mm

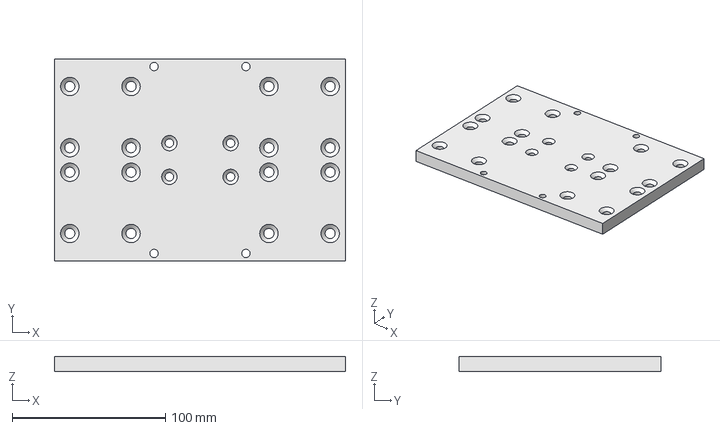
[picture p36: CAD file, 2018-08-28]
Mechanical System/Aluplates/FreeCAD/plate6.FCStd
190.0 x 132.0 x 10.0 mm

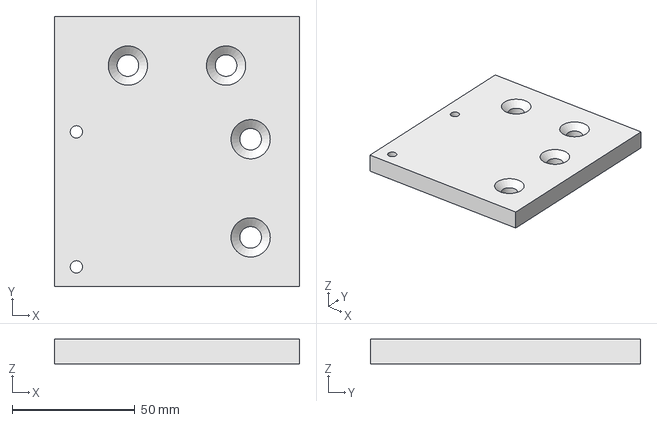
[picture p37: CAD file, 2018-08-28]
Mechanical System/Aluplates/FreeCAD/plate3.FCStd
100.0 x 110.0 x 10.0 mm

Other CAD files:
Accessoires/Lakeshore 460 Gaussmeter probe holder/Holder_Lakeshore_3-axis_withRod_2.stl
Accessoires/SPEAG H1TDS probe holder/H-field_holder_withRod.step
Mechanical System/Aluplates/FreeCAD/plate1.FCStd
Accessoires/Lakeshore 460 Gaussmeter probe holder/Holder_Lakeshore_3-axis_withRod.FCStd
Accessoires/Metrolabs PT2026 probe holder/Holder_NMR_Probe_withRod.FCStd
Accessoires/SPEAG H1TDS probe holder/H-field_holder_withRod.FCStd
Mechanical System/Complete System/complete_system.skp

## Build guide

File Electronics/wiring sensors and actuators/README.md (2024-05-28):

The electronic cabinet was designed to keep backwards compatibility to the connectors of V1.0 in our lab. But it is recommended to change the wiring to standard M12 sensor actuator boxes because this will eventually safe a lot of time in assembly and is general a better solution with less parts.

For cable selection keep in mind, that most cables must be for moving cable chain applications. Use shielded cables for the motors.

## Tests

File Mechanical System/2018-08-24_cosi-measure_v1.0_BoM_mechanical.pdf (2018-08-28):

Number Item | Description | Price | Pcs | Total Price Links
1 Aluminum frame | 40x80L I-Typ Nut 8, 80cm | 17,2 | 6 | 103,2
2 Angle | 40x80 l-Typ Nut 8 + screws | 4,66 | 16 | 74,56
3 Aluminum frame | 40x40L I-Typ Nut 8, 80cm | 8,2 | 3 | 24,6
4 Angle | 40 I-Typ Nut 8 + screws | 2,52 | 12 | 30,24
5 Aluminum frame | 40x80L I-Typ Nut 8, 88cm | 19,66 | 2 | 39,32
5 Slot nut | I-Typ Nut8, M8 | 0,53 | 10 | 5,3
6 Aluminum plate | | 184,45 | 1 | 184,45
7 Screws | DIN7991-M8x20, countersunk | 0,3 | 10 | 3
8 Slot nut | I-Typ Nut8, M5 | 0,53 | 24 | 12,72
9 Supported Rail | TBS20 rail 800mm | 33 | 4 | 132 https://www.dold-mechatronik.de/Linearfuehrung-Supported-Rail-TBS20-800mm-lang

10

Screw | DIN912-M5x20 | 0,13 | 32 | 4,16
11 Linear bearing | TBR20UU | 9,8 | 8 | 78,4
12 Ballscrew + spindle nut block | SFU1605-DM 652mm | 95 | 2 | 190
13 Fixed bearing + motor holder | FLB20-3200 fixed bearing and NEMA23 Motorholder | 53,9 | 2 | 107,8
14 Floating Bearing | LLB20-6200 floating bearing | 14,9 | 2 | 29,8
15 Motor coupler | D25L30 8/8 | 10,5 | 2 | 21
16 Easy-Mechatronics System | | 271,3 | 1 | 271,3
17 Screw | DIN912-M6x20 | 0,14 | 52 | 7,28
18 Screw | DIN7991-M6x20, countersunk | 0,3 | 16 | 4,8 https://www.dold-mechatronik.de/DIN-7991-Senkschraube-mit-Innensechskant-88-verzinkt-M6x20
19 Bolt | DIN912-M5x30 | 0,17 | 20 | 3,4
20 Screw | DIN7991-M5x20, countersunk | 0,3 | 4 | 1,2 https://www.dold-mechatronik.de/DIN-7991-Senkschraube-mit-Innensechskant-88-verzinkt-M6x20
21 Hexagon nut | DIN934-M5 | 0,15 | 24 | 3,6
22 distance holder | 1mm for TBR20UU linear bearing | 1,5 | 4 | 6
23 distance holder | 1mm for ballscrew block | 1,5 | 2 | 3
| Total cost mechanical subsystem: | 1341,13

https://www.dold-mechatronik.de/Aluminiumprofil-40x80L-I-Typ-Nut-8-Standardlaengen-215-EUR-mhttps://www.dold-mechatronik.de/Winkel-40x80-I-Typ-Nut-8-inkl-Befestigungssatzhttps://www.dold-mechatronik.de/Aluminiumprofil-40x40L-I-Typ-Nut-8-Standardlaengen-1025-EUR-mhttps://www.dold-mechatronik.de/Stahlwinkel-40-I-Typ-Nut-8-inkl-Befestigungssatzhttps://www.dold-mechatronik.de/Aluminiumprofil-40x80L-I-Typ-Nut-8-ZUSCHNITT-bis-1200-mm-2200-EUR-m-030-EUR-pro-Schnitthttps://www.dold-mechatronik.de/Nutenstein-mit-Steg-I-Typ-Nut-8-Gewindedurchmesser-waehlbar
AlCuMg1, EN AW-2017A.EN AW-AlCu4MgSi(A), T451 EN 485-
1.2.3 | www.gemmel-metalle.de
| https://www.dold-mechatronik.de/DIN-7991-Senkschraube-mit-Innensechskant-88-verzinkt
| https://www.dold-mechatronik.de/Nutenstein-mit-Steg-I-Typ-Nut-8-Gewindedurchmesser-waehlbar

https://www.dold-mechatronik.de/DIN-912-Zylinderschraube-mit-Innensechskant-88-verzinkthttps://www.dold-mechatronik.de/Linearlager-20mm-TBR20UU-offen-Spiel-einstellbarhttps://www.dold-mechatronik.de/SET-Kugelumlaufspindel-SFU1605-DM-642mm-mit-Spindelmutterblock-fuer-Easy-Mechatronics-System-1620A-L600https://www.dold-mechatronik.de/Festlagereinheit-FLB20-3200-inkl-Motorhalter-NEMA23-Easy-Mechatronics-System-1620Bhttps://www.dold-mechatronik.de/Loslagereinheit-LLB20-6200-Easy-Mechatronics-System-1620Bhttps://www.dold-mechatronik.de/Wellenkupplung-XB-flexibel-D25L30-800-800mm
Linear axis configuration: 1x fixed bearing and motor holder NEMA23, 1x floating bearing, 4x linear bearings SCJ20UU, 2x
präzisionshaft 20mm h6 840mm, 4x shaftholder SH20, 1x
ballscrew with spindle nut block SFU1605-DM 852mm, 1x shaft
coupling 8/8mm D25L30 | https://www.dold-mechatronik.de/Linearachse-Konfigurator-Easy-Mechatronics-System-1620B
| https://www.dold-mechatronik.de/DIN-912-Zylinderschraube-mit-Innensechskant-88-verzinkt
| https://www.dold-mechatronik.de/DIN-912-Zylinderschraube-mit-Innensechskant-88-verzinkt
| https://www.dold-mechatronik.de/DIN-934-Sechskantmutter-8-verzinkt
| https://www.dold-mechatronik.de/Distanzblech-1mm-fuer-TBR20UU
| https://www.dold-mechatronik.de/Distanzblech-1mm-fuer-TR-Muttern-mit-Gehaeuse-16x4-und-16x8-sowie-Spindelmuttergehaeuse-HSFU1605

https://www.dold-mechatronik.de/Linearfuehrung-Supported-Rail-TBS20-800mm-lang

https://www.dold-mechatronik.de/DIN-7991-Senkschraube-mit-Innensechskant-88-verzinkt-M6x20

https://www.dold-mechatronik.de/DIN-7991-Senkschraube-mit-Innensechskant-88-verzinkt-M6x20https://www.dold-mechatronik.de/Aluminiumprofil-40x80L-I-Typ-Nut-8-Standardlaengen-215-EUR-mhttps://www.dold-mechatronik.de/Winkel-40x80-I-Typ-Nut-8-inkl-Befestigungssatzhttps://www.dold-mechatronik.de/Aluminiumprofil-40x40L-I-Typ-Nut-8-Standardlaengen-1025-EUR-mhttps://www.dold-mechatronik.de/Stahlwinkel-40-I-Typ-Nut-8-inkl-Befestigungssatzhttps://www.dold-mechatronik.de/Aluminiumprofil-40x80L-I-Typ-Nut-8-ZUSCHNITT-bis-1200-mm-2200-EUR-m-030-EUR-pro-Schnitthttps://www.dold-mechatronik.de/Nutenstein-mit-Steg-I-Typ-Nut-8-Gewindedurchmesser-waehlbar

www.gemmel-metalle.de
https://www.dold-mechatronik.de/DIN-7991-Senkschraube-mit-Innensechskant-88-verzinkthttps://www.dold-mechatronik.de/Nutenstein-mit-Steg-I-Typ-Nut-8-Gewindedurchmesser-waehlbar

https://www.dold-mechatronik.de/DIN-912-Zylinderschraube-mit-Innensechskant-88-verzinkthttps://www.dold-mechatronik.de/Linearlager-20mm-TBR20UU-offen-Spiel-einstellbarhttps://www.dold-mechatronik.de/SET-Kugelumlaufspindel-SFU1605-DM-642mm-mit-Spindelmutterblock-fuer-Easy-Mechatronics-System-1620A-L600https://www.dold-mechatronik.de/Festlagereinheit-FLB20-3200-inkl-Motorhalter-NEMA23-Easy-Mechatronics-System-1620Bhttps://www.dold-mechatronik.de/Loslagereinheit-LLB20-6200-Easy-Mechatronics-System-1620Bhttps://www.dold-mechatronik.de/Wellenkupplung-XB-flexibel-D25L30-800-800mm

https://www.dold-mechatronik.de/Linearachse-Konfigurator-Easy-Mechatronics-System-1620Bhttps://www.dold-mechatronik.de/DIN-912-Zylinderschraube-mit-Innensechskant-88-verzinkt

https://www.dold-mechatronik.de/DIN-912-Zylinderschraube-mit-Innensechskant-88-verzinkt

https://www.dold-mechatronik.de/DIN-934-Sechskantmutter-8-verzinkt
https://www.dold-mechatronik.de/Distanzblech-1mm-fuer-TBR20UUhttps://www.dold-mechatronik.de/Distanzblech-1mm-fuer-TR-Muttern-mit-Gehaeuse-16x4-und-16x8-sowie-Spindelmuttergehaeuse-HSFU1605

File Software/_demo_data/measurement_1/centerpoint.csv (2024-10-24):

2.541810307368860151e+02
1.499642973217378312e+02
2.774049214601912468e+02

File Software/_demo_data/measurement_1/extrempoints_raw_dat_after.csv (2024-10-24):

X[mm] | Y[mm] | Z[mm] | Bx[mT] | By[mT] | Bz[mT]
254.18 | 239.96 | 277.40 | -47.566000 | -2.077000 | -0.215000
344.18 | 149.96 | 277.40 | -47.588000 | -2.045000 | -0.270000
254.18 | 59.96 | 277.40 | -47.609000 | -2.117000 | -0.282000
164.18 | 149.96 | 277.40 | -47.575000 | -2.088000 | -0.292000
254.18 | 149.96 | 367.40 | -47.623000 | -2.080000 | -0.363000
254.18 | 149.96 | 277.40 | -47.601000 | -2.084000 | -0.265000
254.18 | 149.96 | 187.40 | -47.579000 | -2.137000 | -0.222000

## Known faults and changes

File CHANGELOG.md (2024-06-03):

# Changelog

- 2.0
    - Electronics changed to Rasperry Pi and Rumba32
    - Other simplifications e.g. in the power management board
    - Up to 6x stepper motor drivers
    - Improved safety concept with hardware safe-torque-off and soft and hard limit switches
    - New software
- 1.0
    - Electronics based on Beagle Bone Black and BeBoPr++
    - outdated

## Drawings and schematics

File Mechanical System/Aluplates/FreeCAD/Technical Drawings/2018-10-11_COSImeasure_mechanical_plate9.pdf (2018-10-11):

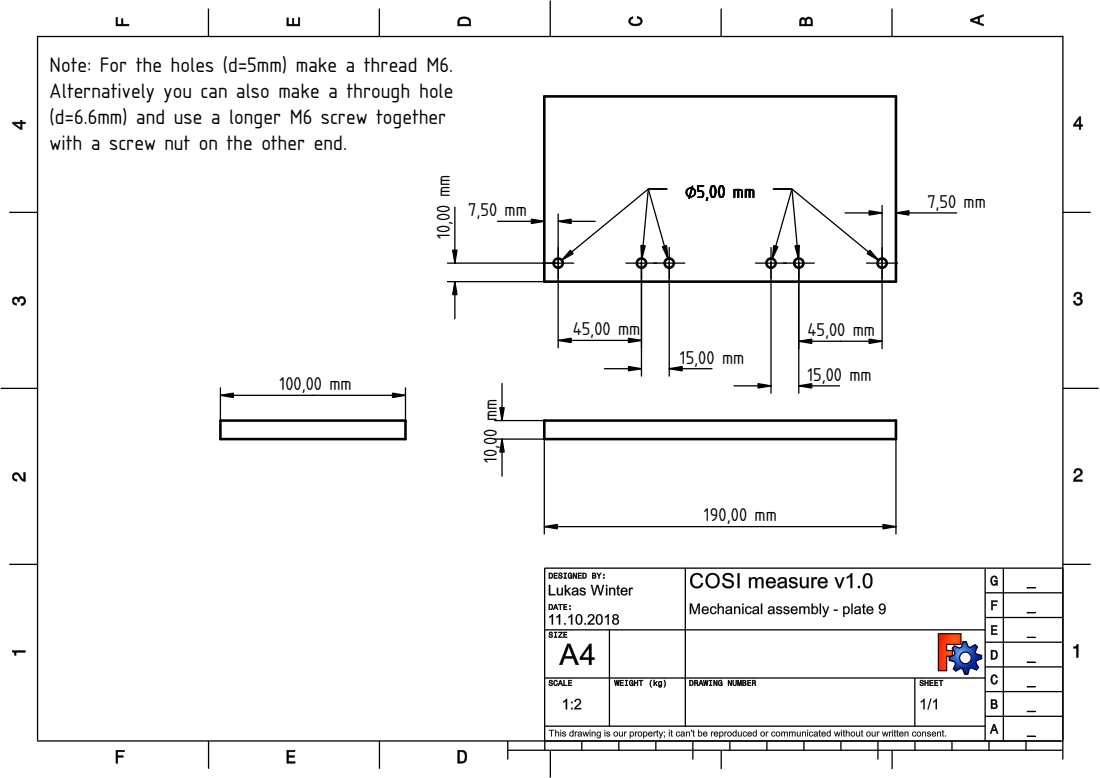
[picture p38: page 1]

Note: For the holes (d=5mm) make a thread M6. Alternatively you can also make a through hole

(d=6.6mm) and use a longer M6 screw together
with a screw nut on the other end.

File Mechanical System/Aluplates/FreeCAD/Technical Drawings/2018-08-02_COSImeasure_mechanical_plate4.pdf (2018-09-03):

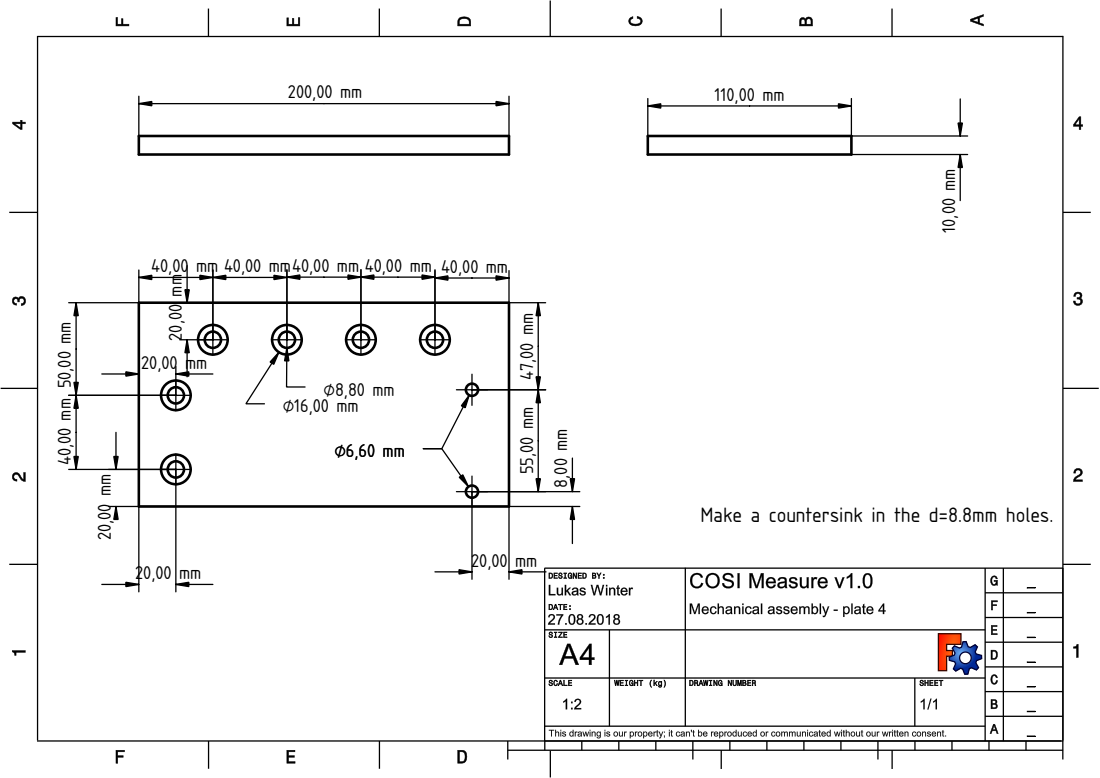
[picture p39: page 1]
10,00 mm 110,00 mm Make a countersink in the d=8.8mm holes.

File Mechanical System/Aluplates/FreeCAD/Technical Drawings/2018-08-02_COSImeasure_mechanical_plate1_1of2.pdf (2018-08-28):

54,00 mm

75,00 mm

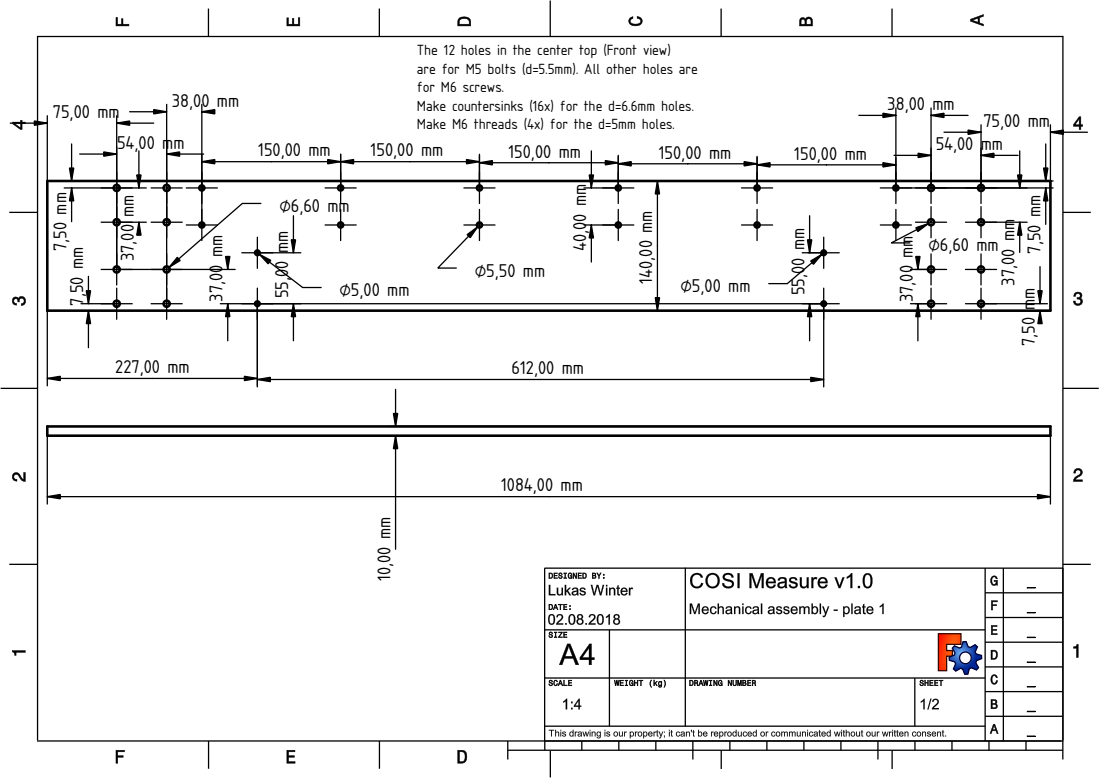
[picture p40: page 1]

The 12 holes in the center top (Front view)
are for M5 bolts (d=5.5mm). All other holes are
for M6 screws. Make countersinks (16x) for the d=6.6mm holes. Make M6 threads (4x) for the d=5mm holes.

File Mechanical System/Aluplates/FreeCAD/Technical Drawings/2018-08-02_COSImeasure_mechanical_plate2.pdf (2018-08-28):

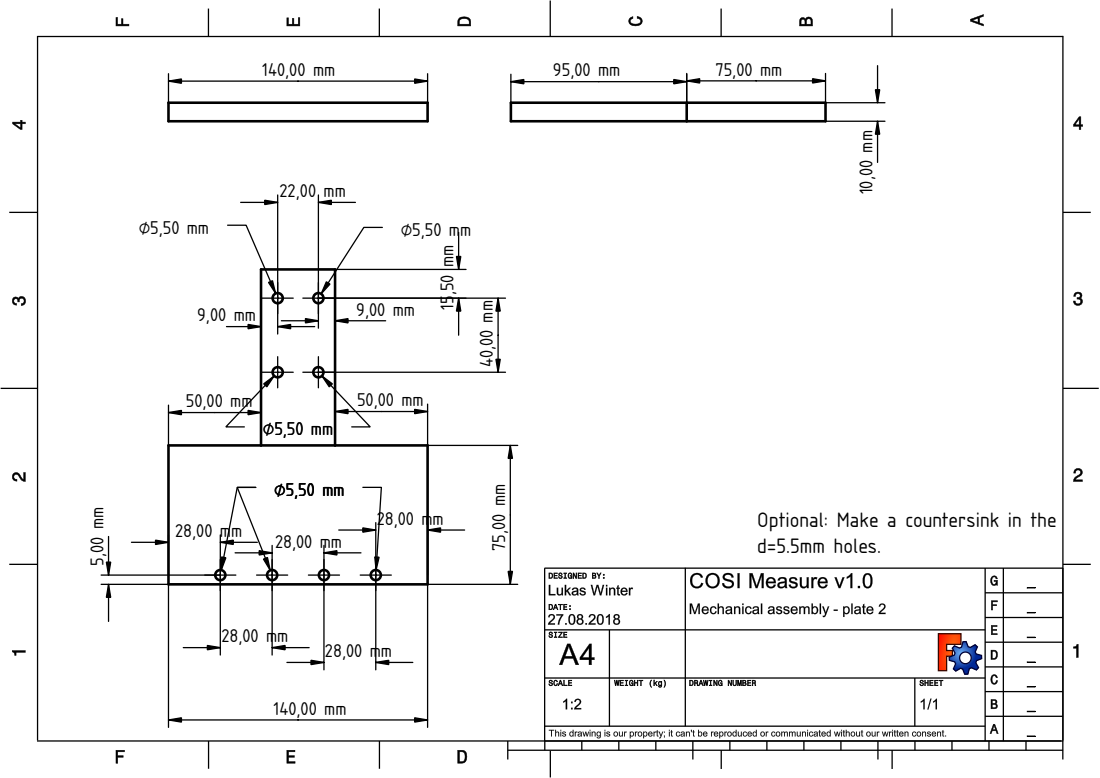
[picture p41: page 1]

Optional: Make a countersink in the
d=5.5mm holes.

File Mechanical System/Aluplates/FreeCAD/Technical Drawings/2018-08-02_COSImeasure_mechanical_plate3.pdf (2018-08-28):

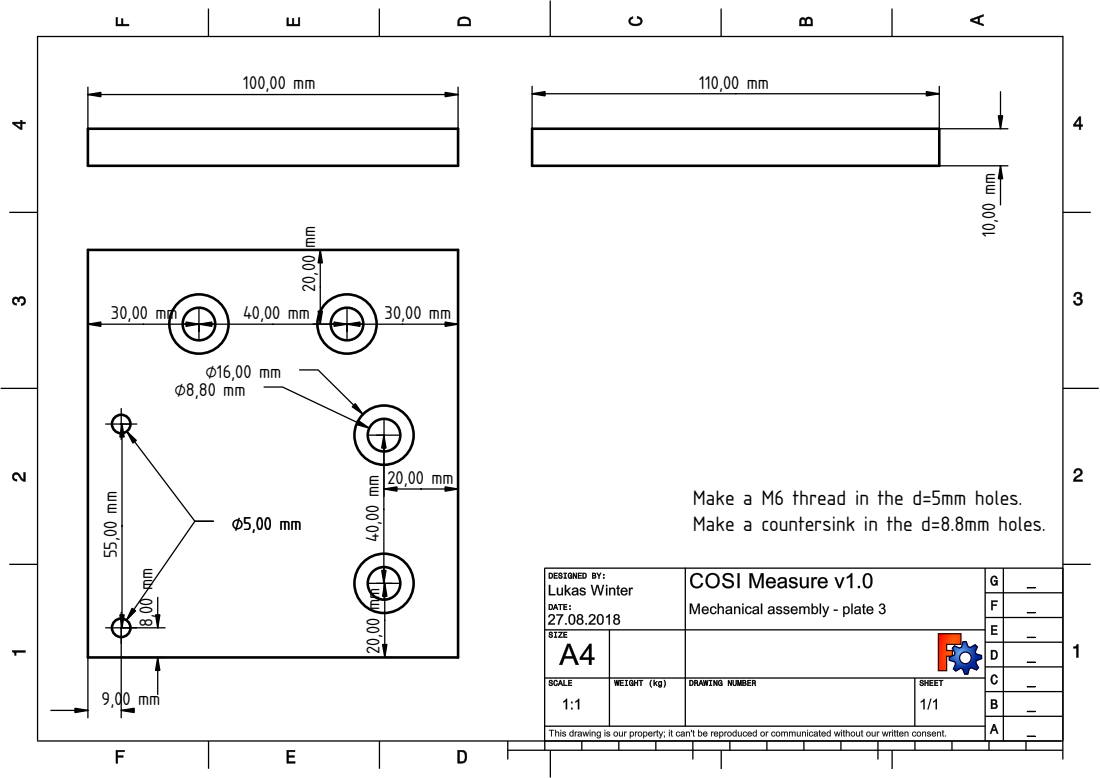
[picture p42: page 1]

Make a M6 thread in the d=5mm holes. Make a countersink in the d=8.8mm holes.

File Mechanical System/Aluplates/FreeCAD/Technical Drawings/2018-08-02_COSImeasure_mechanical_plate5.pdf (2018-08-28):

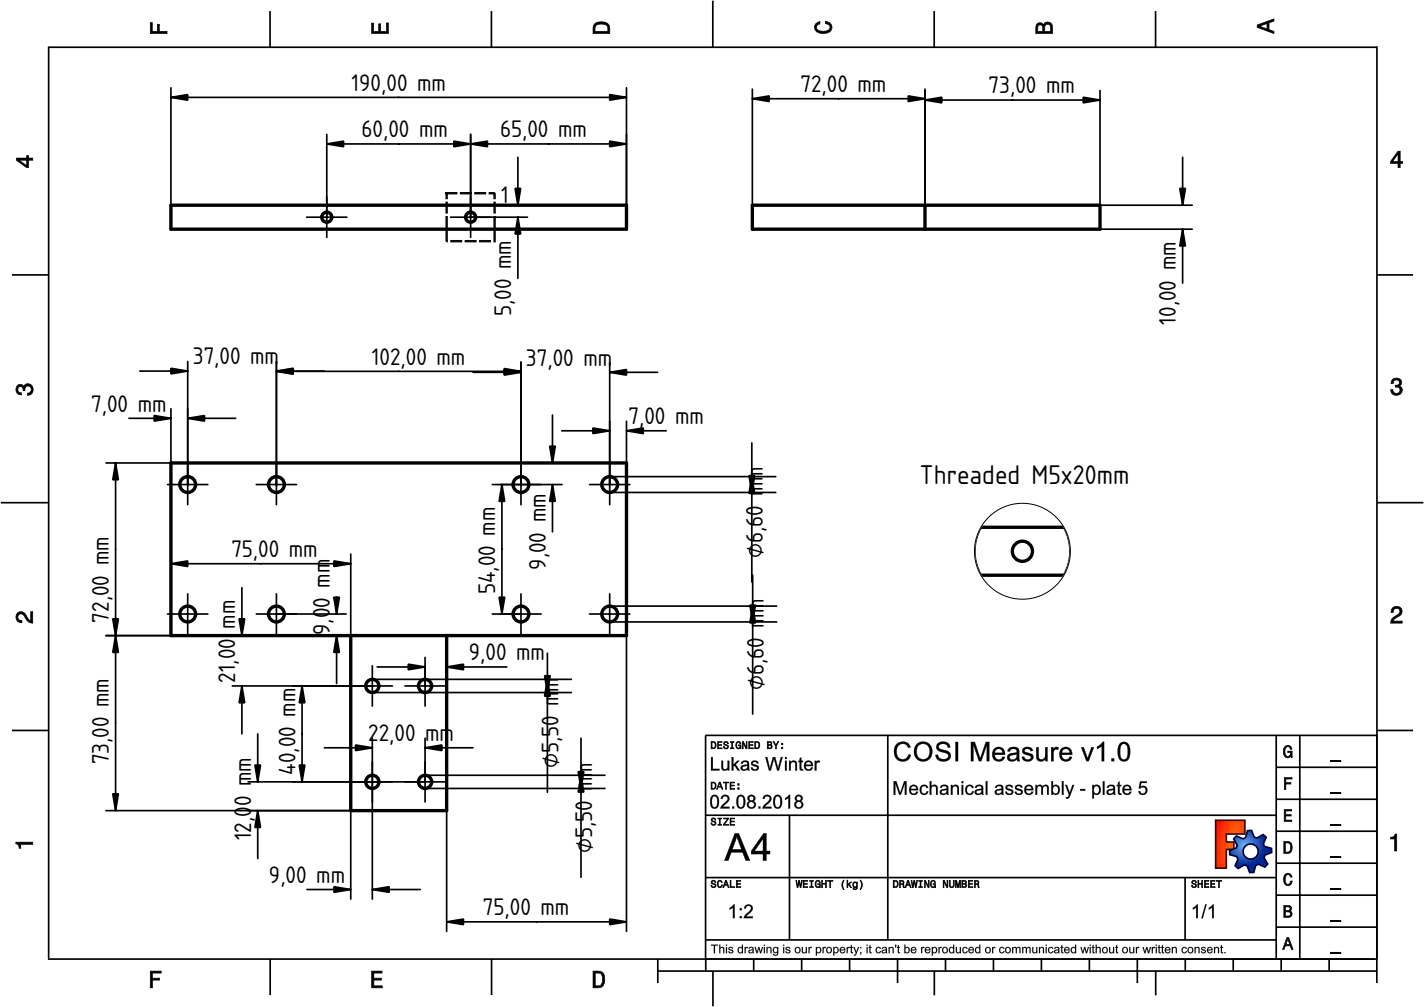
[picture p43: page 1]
Threaded M5x20mm

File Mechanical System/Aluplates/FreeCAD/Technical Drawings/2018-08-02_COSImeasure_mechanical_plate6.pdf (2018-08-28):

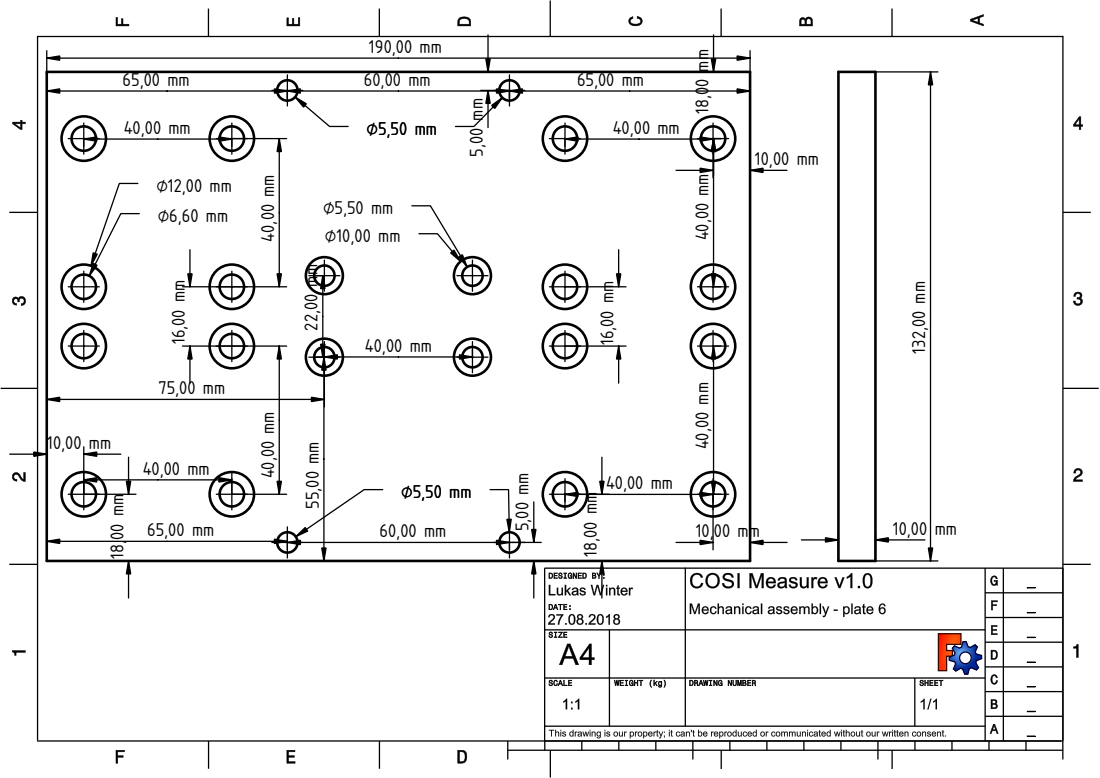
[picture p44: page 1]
mm ¹³²,00 mm

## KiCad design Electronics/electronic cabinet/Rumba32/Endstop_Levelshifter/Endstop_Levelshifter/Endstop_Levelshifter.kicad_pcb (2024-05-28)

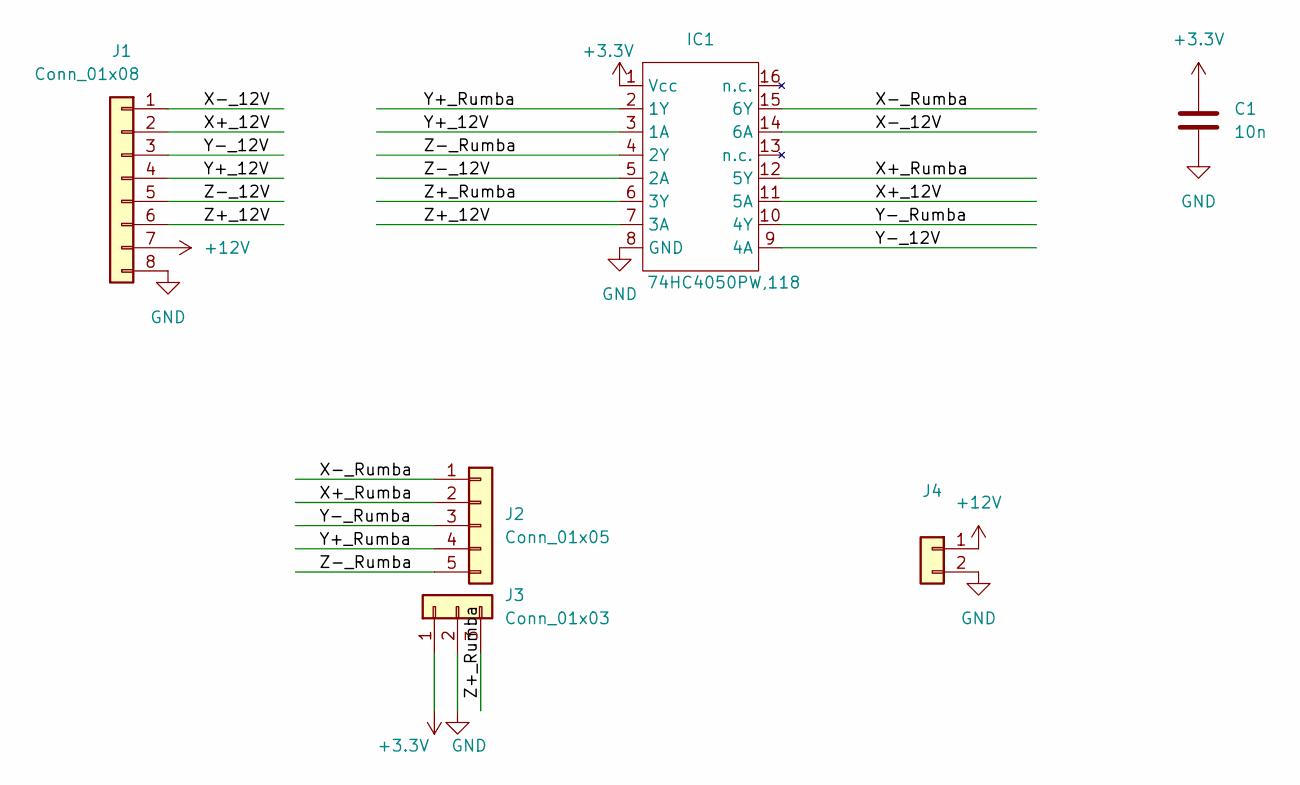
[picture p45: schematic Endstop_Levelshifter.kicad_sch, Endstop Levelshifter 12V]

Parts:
C1: 10n; C_0805_2012Metric_Pad1.18x1.45mm_HandSolder
IC1: 74HC4050PW,118; TSSOP-16_4.4x5mm_P0.65mm
J1: Conn_01x08; 691210910008
J2: Conn_01x05; PinSocket_1x05_P2.54mm_Vertical
J3: Conn_01x03; PinSocket_1x03_P2.54mm_Vertical
J4: Conn_01x02; PinHeader_1x02_P2.54mm_Horizontal

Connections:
+3.3V: C1.1, IC1.1 (Vcc), J3.1
+12V: J1.7, J4.1
/X+_12V: IC1.11 (5A), J1.2
/X+_Rumba: IC1.12 (5Y), J2.2
/X-_12V: IC1.14 (6A), J1.1
/X-_Rumba: IC1.15 (6Y), J2.1
/Y+_12V: IC1.3 (1A), J1.4
/Y+_Rumba: IC1.2 (1Y), J2.4
/Y-_12V: IC1.9 (4A), J1.3
/Y-_Rumba: IC1.10 (4Y), J2.3
/Z+_12V: IC1.7 (3A), J1.6
/Z+_Rumba: IC1.6 (3Y), J3.3
/Z-_12V: IC1.5 (2A), J1.5
/Z-_Rumba: IC1.4 (2Y), J2.5
GND: C1.2, IC1.8 (GND), J1.8, J3.2, J4.2

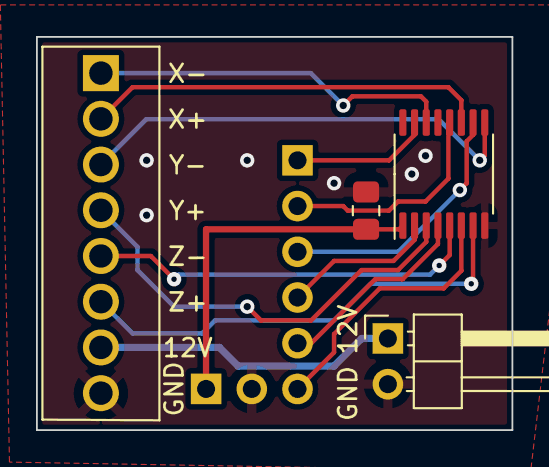
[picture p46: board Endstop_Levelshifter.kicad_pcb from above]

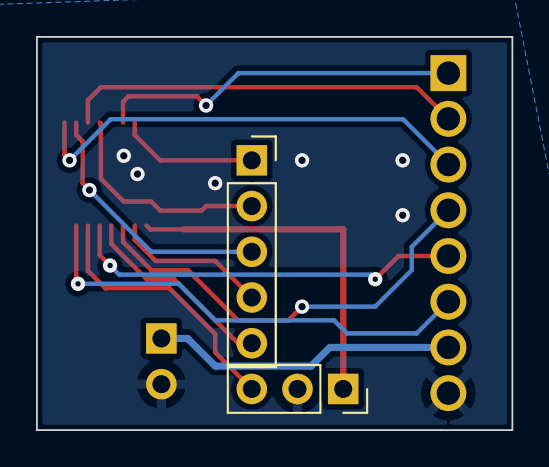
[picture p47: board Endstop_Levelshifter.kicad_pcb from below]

Board: 2 copper layers, 26.4 x 21.8 mm, 6 parts (2 on the bottom side), 15 nets.

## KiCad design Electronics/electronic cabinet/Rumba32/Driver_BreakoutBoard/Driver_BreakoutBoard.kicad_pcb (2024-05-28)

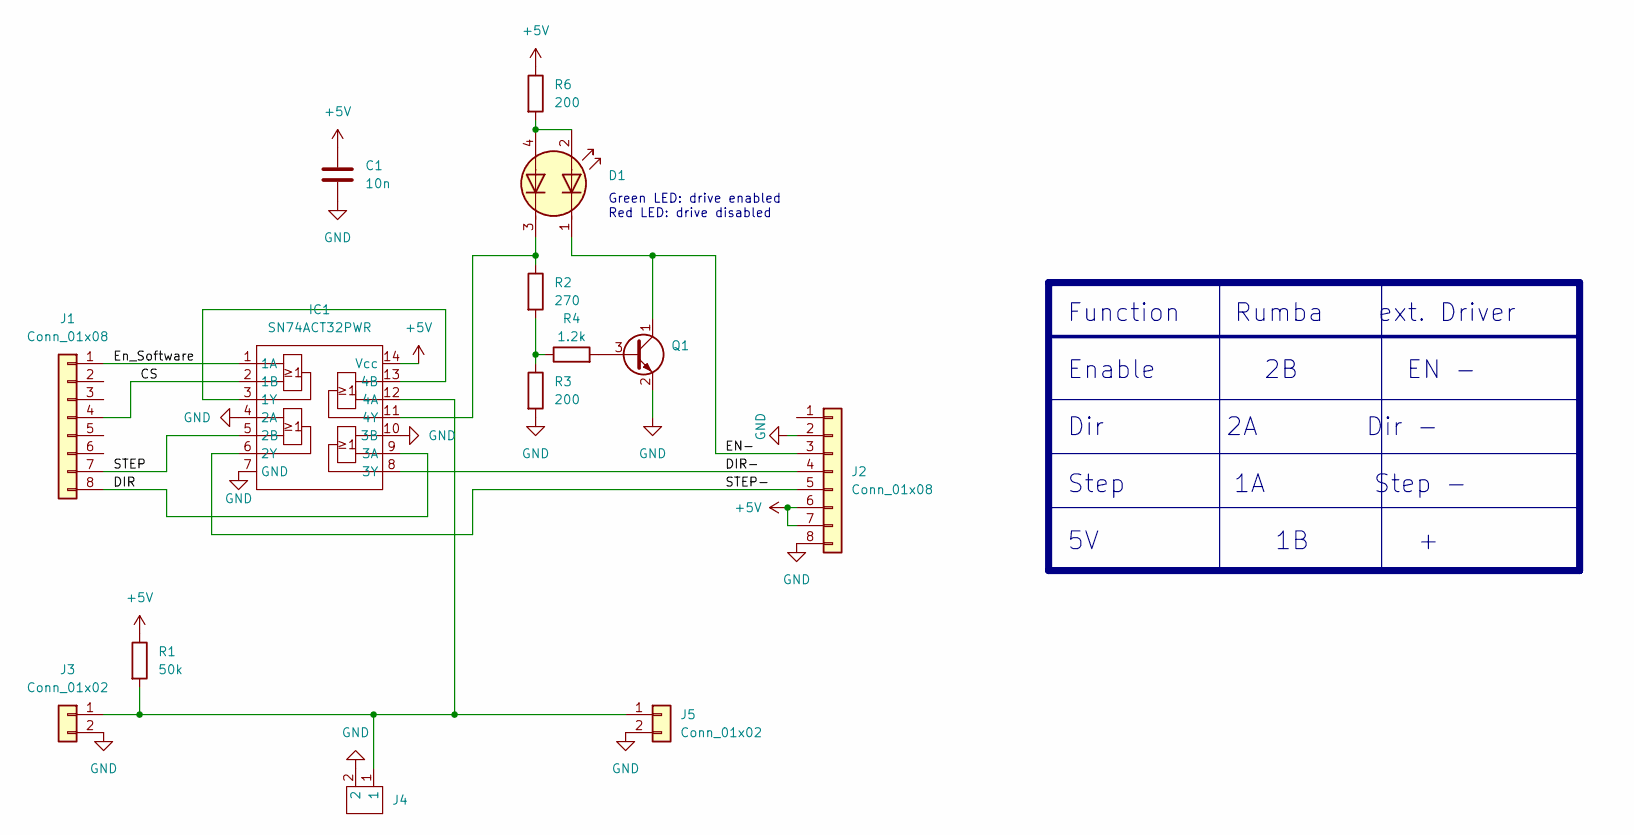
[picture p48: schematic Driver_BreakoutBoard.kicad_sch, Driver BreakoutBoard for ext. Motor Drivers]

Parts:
C1: 10n; C_0805_2012Metric_Pad1.18x1.45mm_HandSolder
D1: LED_Dual; LED_Kingbright_AAA3528ESGCT
IC1: SN74ACT32PWR; SOT402-1_NXP-M
J1, J2: Conn_01x08; PinHeader_1x08_P2.54mm_Vertical
J3, J5: Conn_01x02; PinHeader_1x02_P2.54mm_Vertical
J4: 0393570002
Q1: Q_NPN_CEB; SOT-23_Handsoldering
R1: 50k; R_0805_2012Metric_Pad1.20x1.40mm_HandSolder
R2: 270; R_0805_2012Metric_Pad1.20x1.40mm_HandSolder
R3, R6: 200; R_0805_2012Metric_Pad1.20x1.40mm_HandSolder
R4: 1.2k; R_0805_2012Metric_Pad1.20x1.40mm_HandSolder

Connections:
+5V: C1.1, IC1.14 (Vcc), J2.6, J2.7, R1.1, R6.1
/CS: IC1.2 (1B), J1.4
/DIR: IC1.9 (3A), J1.8
/DIR-: IC1.8 (3Y), J2.4
/EN-: D1.1 (A1), J2.3, Q1.1 (C)
/En_Software: IC1.1 (1A), J1.1
/STEP: IC1.5 (2B), J1.7
/STEP-: IC1.6 (2Y), J2.5
GND: C1.2, IC1.4 (2A), IC1.7 (GND), IC1.10 (3B), J2.2, J2.8, J3.2, J4.2, J5.2, Q1.2 (E), R3.2
unnamed: D1.3 (A2), IC1.11 (4Y), R2.1
unnamed: IC1.3 (1Y), IC1.13 (4B)
unnamed: IC1.12 (4A), J3.1, J4.1, J5.1, R1.2
unnamed: Q1.3 (B), R4.2
unnamed: R2.2, R3.1, R4.1
unnamed: D1.2 (K1), D1.4 (K2), R6.2

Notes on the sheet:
Function Rumba ext. Driver Enable 2B EN - Dir 2A Dir - Step 1A Step - 5V 1B +
Green LED: drive enabled Red LED: drive disabled

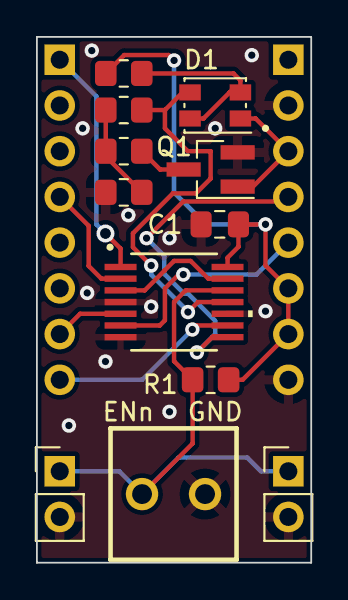
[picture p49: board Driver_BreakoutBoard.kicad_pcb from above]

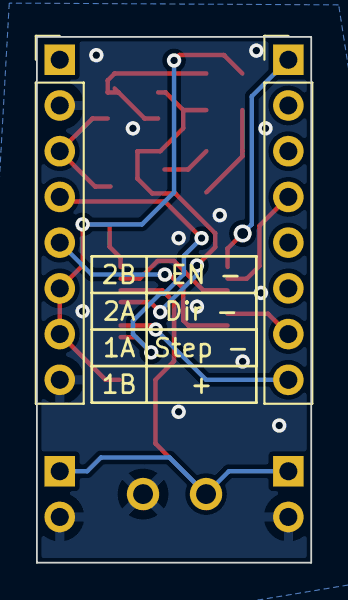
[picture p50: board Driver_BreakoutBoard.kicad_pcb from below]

Board: 2 copper layers, 15.2 x 29.2 mm, 14 parts (2 on the bottom side), 15 nets.

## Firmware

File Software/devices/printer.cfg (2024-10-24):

# This file contains common pin mappings for MKS RUMBA32 boards.  To use
# this config, the firmware should be compiled for the STMicroelectronics STM32,
# Processor model STM32F446, Clock Reference 12 MHz crystal.

# See docs/Config_Reference.md for a description of parameters.

[mcu]
#serial: 1d50:614e
serial: /dev/serial/by-id/usb-Klipper_stm32f446xx_12345-if00
#serial: /dev/serial0
#   The serial port to connect to the MCU. If unsure (or if it
#   changes) see the "Where's my serial port?" section of the FAQ.
#   This parameter must be provided when using a serial port.
baud: 250000
#   The baud rate to use. The default is 250000.
#canbus_uuid:
#   If using a device connected to a CAN bus then this sets the unique
#   chip identifier to connect to. This value must be provided when using
#   CAN bus for communication.
#canbus_interface:
#   If using a device connected to a CAN bus then this sets the CAN
#   network interface to use. The default is 'can0'.
restart_method: command
#   This controls the mechanism the host will use to reset the
#   micro-controller. The choices are 'arduino', 'cheetah', 'rpi_usb',
#   and 'command'. The 'arduino' method (toggle DTR) is common on
#   Arduino boards and clones. The 'cheetah' method is a special
#   method needed for some Fysetc Cheetah boards. The 'rpi_usb' method
#   is useful on Raspberry Pi boards with micro-controllers powered
#   over USB - it briefly disables power to all USB ports to
#   accomplish a micro-controller reset. The 'command' method involves
#   sending a Klipper command to the micro-controller so that it can
#   reset itself. The default is 'arduino' if the micro-controller
#   communicates over a serial port, 'command' otherwise.


[printer]
kinematics: cartesian
#   The type of printer in use. This option may be one of: cartesian,
#   corexy, corexz, hybrid_corexy, hybrid_corexz, rotary_delta, delta,
#   deltesian, polar, winch, or none. This parameter must be specified.
max_velocity: 130
#   Maximum velocity (in mm/s) of the toolhead (relative to the
#   print). This parameter must be specified.
max_accel: 50
#   Maximum acceleration (in mm/s^2) of the toolhead (relative to the
#   print). This parameter must be specified.
#max_accel_to_decel:
#   A pseudo acceleration (in mm/s^2) controlling how fast the
#   toolhead may go from acceleration to deceleration. It is used to
#   reduce the top speed of short zig-zag moves (and thus reduce
#   printer vibration from these moves). The default is half of
#   max_accel.
#square_corner_velocity: 5.0
#   The maximum velocity (in mm/s) that the toolhead may travel a 90
#   degree corner at. A non-zero value can reduce changes in extruder
#   flow rates by enabling instantaneous velocity changes of the
#   toolhead during cornering. This value configures the internal
#   centripetal velocity cornering algorithm; corners with angles
#   larger than 90 degrees will have a higher cornering velocity while
#   corners with angles less than 90 degrees will have a lower
#   cornering velocity. If this is set to zero then the toolhead will
#   decelerate to zero at each corner. The default is 5mm/s.
max_z_velocity: 110
max_z_accel: 45

#[output_pin !X_Enable]
#pin:!PC11
#   The pin to configure as an output. This parameter must be
#   provided.
#pwm: False

#   Set if the output pin should be capable of pulse-width-modulation.
#   If this is true, the value fields should be between 0 and 1; if it
#   is false the value fields should be either 0 or 1. The default is
#   False.
#static_value:
#   If this is set, then the pin is assigned to this value at startup
#   and the pin can not be changed during runtime. A static pin uses
#   slightly less ram in the micro-controller. The default is to use
#   runtime configuration of pins.
#value:1
#   The value to initially set the pin to during MCU configuration.
#   The default is 0 (for low voltage).

[stepper_x]
step_pin: PA0
#   Step GPIO pin (triggered high). This parameter must be provided.
dir_pin: !PC15
#   Direction GPIO pin (high indicates positive direction). This
#   parameter must be provided.
enable_pin: !PC11
#   Enable pin (default is enable high; use ! to indicate enable
#   low). If this parameter is not provided then the stepper motor
#   driver must always be enabled.
rotation_distance: 5
#   Distance (in mm) that the axis travels with one full rotation of
#   the stepper motor (or final gear if gear_ratio is specified).
#   This parameter must be provided.
microsteps: 8 #64 #128
#   The number of microsteps the stepper motor driver uses. This
#   parameter must be provided.
full_steps_per_rotation: 200
#   The number of full steps for one rotation of the stepper motor.
#   Set this to 200 for a 1.8 degree stepper motor or set to 400 for a
#   0.9 degree motor. The default is 200.
#gear_ratio:
#   The gear ratio if the stepper motor is connected to the axis via a
#   gearbox. For example, one may specify "5:1" if a 5 to 1 gearbox is
#   in use. If the axis has multiple gearboxes one may specify a comma
#   separated list of gear ratios (for example, "57:11, 2:1"). If a
#   gear_ratio is specified then rotation_distance specifies the
#   distance the axis travels for one full rotation of the final gear.
#   The default is to not use a gear ratio.
step_pulse_duration: 0.0000035 # 3,5 µs
#   The minimum time between the step pulse signal edge and the
#   following "unstep" signal edge. This is also used to set the
#   minimum time between a step pulse and a direction change signal.
#   The default is 0.000000100 (100ns) for TMC steppers that are
#   configured in UART or SPI mode, and the default is 0.000002 (which
#   is 2us) for all other steppers.
endstop_pin: !PB12
#   Endstop switch detection pin. If this endstop pin is on a
#   different mcu than the stepper motor then it enables "multi-mcu
#   homing". This parameter must be provided for the X, Y, and Z
#   steppers on cartesian style printers.
#position_min: 0
#   Minimum valid distance (in mm) the user may command the stepper to
#   move to.  The default is 0mm.
position_endstop: 0
#   Location of the endstop (in mm). This parameter must be provided
#   for the X, Y, and Z steppers on cartesian style printers.
position_max: 497
#   Maximum valid distance (in mm) the user may command the stepper to
#   move to. This parameter must be provided for the X, Y, and Z
#   steppers on cartesian style printers.
homing_speed: 10
#   Maximum velocity (in mm/s) of the stepper when homing. The default
#   is 5mm/s.
homing_retract_dist: 10
#   Distance to backoff (in mm) before homing a second time during
#   homing. Set this to zero to disable the second home. The default
#   is 5mm.
homing_retract_speed: 7
#   Speed to use on the retract move after homing in case this should
#   be different from the homing speed, which is the default for this
#   parameter
second_homing_speed: 3
#   Velocity (in mm/s) of the stepper when performing the second home.
#   The default is homing_speed/2.
homing_positive_dir: false
#   If true, homing will cause the stepper to move in a positive
#   direction (away from zero); if false, home towards zero. It is
#   better to use the default than to specify this parameter. The
#   default is true if position_endstop is near position_max and false
#   if near position_min.
##gear_ratio:
#   The gear ratio if the stepper motor is connected to the axis via a
#   gearbox. For example, one may specify "5:1" if a 5 to 1 gearbox is
#   in use. If the axis has multiple gearboxes one may specify a comma
#   separated list of gear ratios (for example, "57:11, 2:1"). If a
#   gear_ratio is specified then rotation_distance specifies the
#   distance the axis travels for one full rotation of the final gear.
#   The default is to not use a gear ratio.

[stepper_y]
step_pin: PE5
dir_pin: PE6
enable_pin: !PE3
microsteps: 8 #64
rotation_distance: 5
step_pulse_duration: 0.0000035 # 3,5 µs
endstop_pin: !PD8 #!PB15
position_endstop: 460 # 0
position_max: 460
homing_speed: 10
homing_retract_dist: 10
homing_retract_speed: 7
second_homing_speed: 3
homing_positive_dir: true # false


[stepper_z]
step_pin: PE1
dir_pin: !PE2
enable_pin: !PB7
microsteps: 8 #64
rotation_distance: 5
step_pulse_duration: 0.0000035 # 3,5 µs
endstop_pin: !PD9
position_endstop: 0
position_max: 610
homing_speed: 10
homing_retract_dist: 10
homing_retract_speed: 7
second_homing_speed: 3
homing_positive_dir: false


[extruder]
step_pin: PB5
dir_pin: PB6
enable_pin: !PC12
microsteps: 16
rotation_distance: 33.500
nozzle_diameter: 0.400
filament_diameter: 1.750
heater_pin: PC6
sensor_type: NTC 100K MGB18-104F39050L32
sensor_pin: PC4
control: pid
pid_Kp: 22.2
pid_Ki: 1.08
pid_Kd: 114
min_temp: 0
max_temp: 2500

#[extruder1]
#step_pin: PD6
#dir_pin: PD7
#enable_pin: !PD4
#heater_pin: PC7
#sensor_pin: PC3
#...

#[extruder2]
#step_pin: PD2
#dir_pin: PD3
#enable_pin: !PD0
#heater_pin: PC8
#sensor_pin: PC2
#...

[heater_bed]
heater_pin: PA1
sensor_type: NTC 100K MGB18-104F39050L32
sensor_pin: PC0
control: watermark
min_temp: 0
max_temp: 130

[fan]
pin: PC9

#[heater_fan fan1]
#pin: PA8

# Kill-Switch
[gcode_button kill_switch]
pin: PC5
press_gcode: M112


########################################
# EXP1 / EXP2 (display) pins
########################################

[board_pins]
aliases:
    # EXP1 header
    EXP1_1=PE8, EXP1_3=PE9, EXP1_5=PE12, EXP1_7=PE14, EXP1_9=<GND>,
    EXP1_2=PE7, EXP1_4=PE10, EXP1_6=PE13, EXP1_8=PE15, EXP1_10=<5V>,
    # EXP2 header
    EXP2_1=PA6, EXP2_3=PB2, EXP2_5=PB1, EXP2_7=PB0,  EXP2_9=<GND>,
    EXP2_2=PA5, EXP2_4=PA2, EXP2_6=PA7, EXP2_8=<RST>, EXP2_10=PC5,


[output_pin X_CS]
pin: PC14

[output_pin Y_CS]
pin: PE4

[output_pin Z_CS]
pin: PE0

[output_pin E0_CS]
pin: PC13

[output_pin E1_CS]
pin: PD5

[output_pin E2_CS]
pin: PD1


[gcode_macro hard_disable_drives]
description: Disables all motors. Software realizes nothing from it.
gcode:
  G4 P1000
  SET_PIN PIN=X_CS VALUE=1
  SET_PIN PIN=Y_CS VALUE=1
  SET_PIN PIN=Z_CS VALUE=1
  SET_PIN PIN=E0_CS VALUE=1
  SET_PIN PIN=E1_CS VALUE=1
  SET_PIN PIN=E2_CS VALUE=1
  G4 P1000


[gcode_macro hard_enable_drives]
description: Disables all motors. Software realizes nothing from it.
gcode:
  G4 P1000
  SET_PIN PIN=X_CS VALUE=0
  SET_PIN PIN=Y_CS VALUE=0
  SET_PIN PIN=Z_CS VALUE=0
  SET_PIN PIN=E0_CS VALUE=0
  SET_PIN PIN=E1_CS VALUE=0
  SET_PIN PIN=E2_CS VALUE=0
  G4 P1000


[gcode_arcs] #enables G2 and G3


# See the sample-lcd.cfg file for definitions of common LCD displays.


########################################
# TMC2209 configuration
########################################

#[tmc2209 stepper_x]
#uart_pin: PC14
##tx_pin: PA3
#run_current: 0.800
#diag_pin:

#[tmc2209 stepper_y]
#uart_pin: PE4
##tx_pin: PA4
#run_current: 0.800
#diag_pin:

#[tmc2209 stepper_z]
#uart_pin: PE0
##tx_pin: PD13
#run_current: 0.800
#diag_pin:

#[tmc2209 extruder]
#uart_pin: PC13
##tx_pin: PD14
#run_current: 0.600
#diag_pin:

[idle_timeout]
timeout: 1000000000000000000000000

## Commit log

2017-10-10 Initial commit v1.0
    [BOM.xlsx, P1_1084x140x10.skp, P2_170x140x10.skp, P3_100x110x10.skp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]
2017-10-11 Updated BOM and partlist
    [BOM.xlsx, partlist.xlsx]
2018-08-09 Aluplates design files in FreeCAD v0.17
    [plate1.FCStd, plate2.FCStd, plate3.FCStd, plate4.FCStd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]
2018-08-13 Missing dimension added to Aluplate 8
    [plate8.FCStd]
2018-08-13 Missing dimension added to tech drawing
    [plate5.FCStd]
2018-08-13 Missing dimensions added to tech drawing
    [plate2.FCStd]
2018-08-15 updated tech drawings
    [plate4.FCStd]
2018-08-15 tech drawing updated
    [plate6.FCStd]
2018-08-28 Updated mechanical documentation and CAD files of the Aluplates.
    [plate1.FCStd, plate2.FCStd, plate3.FCStd, plate4.FCStd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]
2018-08-28 Updated mechanical assembly documentation
2018-08-28 Updated BoM files
    [2018-08-24_cosi-measure_v1.1_BoM_mechanical.ods, partlist.xlsx]
2018-08-28 naming error corrected
    [2018-08-24_cosi-measure_v1.0_BoM_mechanical.ods]
2018-08-30 small changes in documentation
    [2018-08-24_cosi-measure_v1.0_BoM_mechanical.ods]
2018-09-03 small correction plate 4 and corresponding documentation/BoM
    [2018-08-24_cosi-measure_v1.0_BoM_mechanical.ods, plate4.FCStd]
2018-10-09 Updated BoM electronics file
    [2018-10-09_cosi-measure_v1.0_BoM_electronics.ods, BOM.xlsx]
2018-10-11 Changed hole distance of plate 9
    [plate9.FCStd]
2018-10-11 updated BoM, pin strip mates and cable chain
    [2018-10-09_cosi-measure_v1.0_BoM_electronics.ods]
2018-11-12 Casing files uploaded and BoM updated
    [2018-08-24_cosi-measure_v1.0_BoM_mechanical.ods, 2018-10-09_cosi-measure_v1.0_BoM_electronics.ods, 2018-11-11_cosi-measure-v1.0_casing.FCStd, 2018-11-12_cosi-m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]
2019-01-11 Casing assembly documentation, electrical assembly documentation added, compiled CPLD code added and a bit of reordering.
    [2018-11-12_cosi-measure_v1.0_BoM_electronics.ods, 2019-01-11_cosi-measure_v1.0_BoM_electronics.ods, J5-BOB-R0.drills.xln, P1_1084x140x10.skp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]
2019-01-25 Updated KiCAD + Gerber files of the power managment board.
    [cosi_pwr-B.CrtYd.gbr, cosi_pwr-B.SilkS.gbr, cosi_pwr-Bottom.gbr, cosi_pwr-Edge.Cuts.gbr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]
2019-03-04 documentation update on the J5-Bob
    [2019-01-11_cosi-measure_v1.0_BoM_electronics.ods, 2019-03-04_cosi-measure_v1.0_BoM_electronics.ods, J5-BOB-R0.drills.xln, cosi_pwr-2019-01-25-09-19-00.sch]
2019-04-25 Updated Limitswitchholder files (FreeCAD).
    [2018-11-11_cosi-measure-v1.0_casing.FCStd, LimitSwitchHolder_x-axis_chainholder.fcstd, LimitSwitchHolder_x-axis_chainholder.step, LimitSwitchHolder_x-axis_chai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]
2020-07-07 limit and cable chain holder v2
    More robust limit switch holder and cable chain holder version
2021-08-09 limit switch holder alternatives
    Alternative CAD files for the limit switch holders for the x- and z-axis
    [limit_switch_holder_x-axis_v2.stp, limit_switch_holder_z-axis_v2.stp]
2021-08-09 probe holder CAD files
    CAD files for various probes
    [H-field_holder_withRod.FCStd, H-field_holder_withRod.step, H-field_holder_withRod_2.stl, Holder_Lakeshore_3-axis_withRod.FCStd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]
2024-05-17 adding new electronics
    [2018-11-11_cosi-measure-v1.0_casing.FCStd, 2019-03-04_cosi-measure_v1.0_BoM_electronics.ods, Driver_BreakoutBoard.kicad_pcb, Driver_BreakoutBoard.kicad_sch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]
2024-05-17 removing old limit switches
    [LimitSwitchHolder_x-axis_chainholder.fcstd, LimitSwitchHolder_x-axis_chainholder.step, LimitSwitchHolder_x-axis_chainholder.stl, LimitSwitchHolder_x-minus.fcst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]
2024-05-17 adding notes about cable selection + sensor-actuator bixes
2024-05-17 adding software from https://github.com/rst030/cosi-measure/tree/master/Software/COSI2
    [test.csv]
2024-05-17 adding limit switch holders by Tobias Mohr
    [Sensor Winkel1.stl, Sensor Winkel1_kurz.stl, Sensor Winkel1_kurz_lang.stl]
2024-06-30 Update bom-electronic-cabinet.csv
    Changed enclosure type to NSYS3D6420P.
    [bom-electronic-cabinet.csv]
2024-10-24 Master (#11)
    * rewrote software. no GUI yet
    * adding spherical harmonic decomposition, + code sugar
    * adding reliability to serial communication + code sugar
    * adding magnet types to coord transformations
    * adding cosi 2 magnet V2.1 transformation
    * optimized interface to csv importer
    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
    [centerpoint.csv, extrempoints_raw_dat_after.csv, extrempoints_raw_dat_before.csv, raw_dat.csv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]
